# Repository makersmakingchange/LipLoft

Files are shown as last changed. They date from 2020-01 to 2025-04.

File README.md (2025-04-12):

# Liploft

This project was created to enable a person with limited hand function, such as person with quadraplegia, to operate a radio frequency (RF) remote control drone. The project is based on a [LipSync Wireless](https://github.com/makersmakingchange/LipSync-Wireless), an open-source, mouth operated joystick. The user moves the joystick with their lips and mouth and uses sips and puffs of air on the joystick to interact with the drone remote control.

This GitHub repository will serve as a database for all files and documentation associated with the Liploft project. 

This project is a **work in progress**.

## Table of Contents
- [Overview](#overview)
  * [Approach](#approach)
- [Download](#download)
- [Installation and Setup](#installation-and-setup)
  * [LipSync Wireless](#lipsync-wireless)
  * [Liploft Remote Control Interface](#liploft-remote-control-interface)
  * [Software](#software)
- [Operation](#operation)
  * [Pairing](#pairing)
  * [Controlling the Drone with LipSync](#controlling-the-drone-with-lipsync)
- [Contact Us](#contact-us)

<small><i><a href='http://ecotrust-canada.github.io/markdown-toc/'>Table of contents generated with markdown-toc</a></i></small>
  
## Overview
Liploft requires the following components:

1. A drone
2. The drone's remote control, modified to connect with the LipLoft interface.
3. A [Lipsync Wireless](https://github.com/makersmakingchange/LipSync-Wireless) with LipLoft firmware.

### Approach
The Liploft interface is comprised of a microcontroller, a Bluetooth module, and 4 digital potentiometers. The drone's remote controls is modified by removing the two physical joysticks and connecting the digital potetiometers to create virtual, software controllable joysticks. The Liploft acts as a Bluetooth master, connecting to the LipSync Wireless which acts as a Bluetooth slave. Physical movement of and and sips and puffs through the mouthpiece are digitized, transmitted to the Liploft interface and converted into virtual joystick signals.

## Download

 <table style="width:100%">
  <tr>
    <th>Resource</th>
    <th>Version</th>
    <th>Format</th>
    <th>Link</th>
  </tr>
    <tr>
    <td>Liploft All</td>
    <td>Beta 8</td>
    <td>ZIP</td>
    <td><a href="https://github.com/makersmakingchange/LipLoft/archive/master.zip">LipLoft-master.zip</a></td>
  </tr>
  <tr>
    <td>Liploft Manual</td>
    <td>Version 1.0</td>
    <td>PDF</td>
    <td><a href="https://github.com/makersmakingchange/LipLoft/raw/master/LipLoft_User_Manual.pdf">LipLoft_User_Manual.pdf</a></td>
  </tr>
  <tr>
    <td>Liploft BOM (XLSX)</td>
    <td></td>
    <td>XLSX</td>
    <td><a href="https://github.com/makersmakingchange/LipLoft/raw/master/LipLoft_BOM.xlsx">Liploft_BOM.xlsx</a></td>
  </tr>
  <tr>
    <td>Liploft BOM (CSV)</td>
    <td></td>
    <td>CSV</td>
    <td><a href="https://github.com/makersmakingchange/LipLoft/blob/master/LipLoft_BOM.csv" download target="_blank">Liploft_BOM.csv</a></td>
  </tr>
  <tr>
    <td>Lipsync Liploft Firmware</td>
    <td>1.1</td>
    <td>INO</td>
    <td><a href="https://github.com/makersmakingchange/Liploft/raw/master/Software/LipSync_Liploft_Firmware/LipSync_Liploft_Firmware.ino">LipSync_Liploft_Firmware.ino</a></td>
  </tr>
  <tr>
    <td>Liploft Interface Firmware</td>
    <td>1.9</td>
    <td>INO</td>
    <td><a href="https://github.com/makersmakingchange/Liploft/raw/master/Software/Liploft_Interface_Firmware/Liploft_Interface_Firmware.ino">Liploft_Interface_Firmware.ino</a></td>
  </tr>
  <tr>
    <td>Lipsync Manual Bluetooth Config</td>
    <td></td>
    <td>INO</td>
    <td><a href="https://github.com/makersmakingchange/Liploft/raw/master/Software/Liploft_Bluetooth_Config/Lipsync_Bluetooth_Config/Lipsync_Bluetooth_Config.ino">Lipsync_Bluetooth_Config.ino</a></td>
  </tr>
  <tr>
    <td>Interface Manual Bluetooth Config</td>
    <td></td>
    <td>INO</td>
    <td><a href="https://github.com/makersmakingchange/Liploft/raw/master/Software/Liploft_Bluetooth_Config/Interface_Bluetooth_Config/Interface_Bluetooth_Config.ino">Interface_Bluetooth_Config.ino</a></td>
  </tr>
  <tr>
    <td>Liploft Fritzing Board Layout</td>
    <td>Beta 8</td>
    <td>BRD</td>
    <td><a href="https://raw.githubusercontent.com/makersmakingchange/Liploft/master/Hardware/Electronics/Fritzing/Liploft_Breadboard.fzz">Liploft_Breadboard.fzz</a></td>
  </tr>
  <tr>
    <td>Liploft Interface Board Schematic</td>
    <td>Beta 8</td>
    <td>SCH</td>
    <td><a href="https://raw.githubusercontent.com/makersmakingchange/Liploft/master/Hardware/Electronics/Eagle/Liploft_Schematics.sch">Liploft_Schematics.sch</a></td>
  </tr>
  <tr>
    <td rowspan="3">Liploft Housing_design</td>
    <td rowspan="3">V5</td>
    <td rowspan="3">X3G,STL</td>
    <td><a href="https://raw.githubusercontent.com/makersmakingchange/Liploft/master/Hardware/Housing_design/LipSyncDrone/Don_Encl_v5_ABS_L.x3g">Don_Encl_v5_ABS_L.x3g</a></td>
  </tr>
   <tr>
  <td><a href="https://github.com/makersmakingchange/LipLoft/raw/master/Hardware/Housing_design/Liploft_Top.stl">Liploft_Top.STL</a></td>
  </tr>
 <tr>
  <td><a href="https://github.com/makersmakingchange/LipLoft/raw/master/Hardware/Housing_design/Liploft_Bottom.stl">Liploft_Bottom.STL</a></td>
</tr>
 
</tr>
  <tr>
    <td rowspan="8">Lipsync Housing_design</td>
    <td rowspan="8">2.2d</td>
    <td rowspan="8">STL</td>
    <td><a href="https://raw.githubusercontent.com/makersmakingchange/Liploft/master/Hardware/Housing_design/LipSync_Button.STL">LipSync_Button.STL</a></td>
  </tr>
  <tr>
  <td><a href="https://github.com/makersmakingchange/Liploft/raw/master/Hardware/Housing_design/LipSync_Front_Housing.STL">LipSync_Front_Housing.STL</a></td>
  </tr>
  <tr>
  <td><a href="https://github.com/makersmakingchange/Liploft/raw/master/Hardware/Housing_design/LipSync_Joystick_Base.STL">LipSync_Joystick_Base.STL</a></td>
</tr>
<tr>
  <td><a href="https://github.com/makersmakingchange/Liploft/raw/master/Hardware/Housing_design/LipSync_Joystick_Front.STL">LipSync_Joystick_Front.STL</a></td>
</tr>
<tr>
  <td><a href="https://github.com/makersmakingchange/Liploft/raw/master/Hardware/Housing_design/LipSync_Joystick_Rocker.STL">LipSync_Joystick_Rocker.STL</a></td>
</tr>
<tr>
    <td><a href="https://github.com/makersmakingchange/Liploft/raw/master/Hardware/Housing_design/LipSync_Joystick_Stand.STL">LipSync_Joystick_Stand.STL</a></td>
</tr>
 <tr>
  <td><a href="https://github.com/makersmakingchange/LipLoft/raw/master/Hardware/Housing_design/LipSync_Rear_Housing.stl">LipSync_Rear_Housing.STL</a></td>
</tr>
<tr>
  <td><a href="https://raw.githubusercontent.com/makersmakingchange/Liploft/master/Hardware/Housing_design/Print_Settings.txt">Print_Settings.txt</a></td>
</tr>
</table> 

## Installation and Setup

### LipSync Wireless
1. Obtain a [Lipsync Wireless](https://github.com/makersmakingchange/LipSync-Wireless). There are several options for getting a Lipsync Wireless:
 * Build your own. All the necessary files, software, and assembly guides are available in the [Lipsync Wireless GitHub repository](https://github.com/makersmakingchange/LipSync-Wireless). 
 * Submit a build request through the [Makers Making Change website](https://www.makersmakingchange.com/project/lipsyncwireless/). MMC will attempt to pair you with a local volunteer maker to help build and program one. You'll be responsible for covering the cost of materials and shipping. Depending on your location, there may also be pre-built donated units available at little or no cost.
 * [Order a built LipSync](https://www.makersmakingchange.com/order-built-lipsync/) from the Makers Making Change website.
 
 2. It may be helpful to modify the rear housing of the LipSync Wireless so the LED on the Bluetooth module is visible.

### Liploft Remote Control Interface
The remote control interface requires some permanent modifications to the drone's remote control and the addition of several hardware components.

* Setup the circuit in breadboard according to the following diagram:

<p align="center">
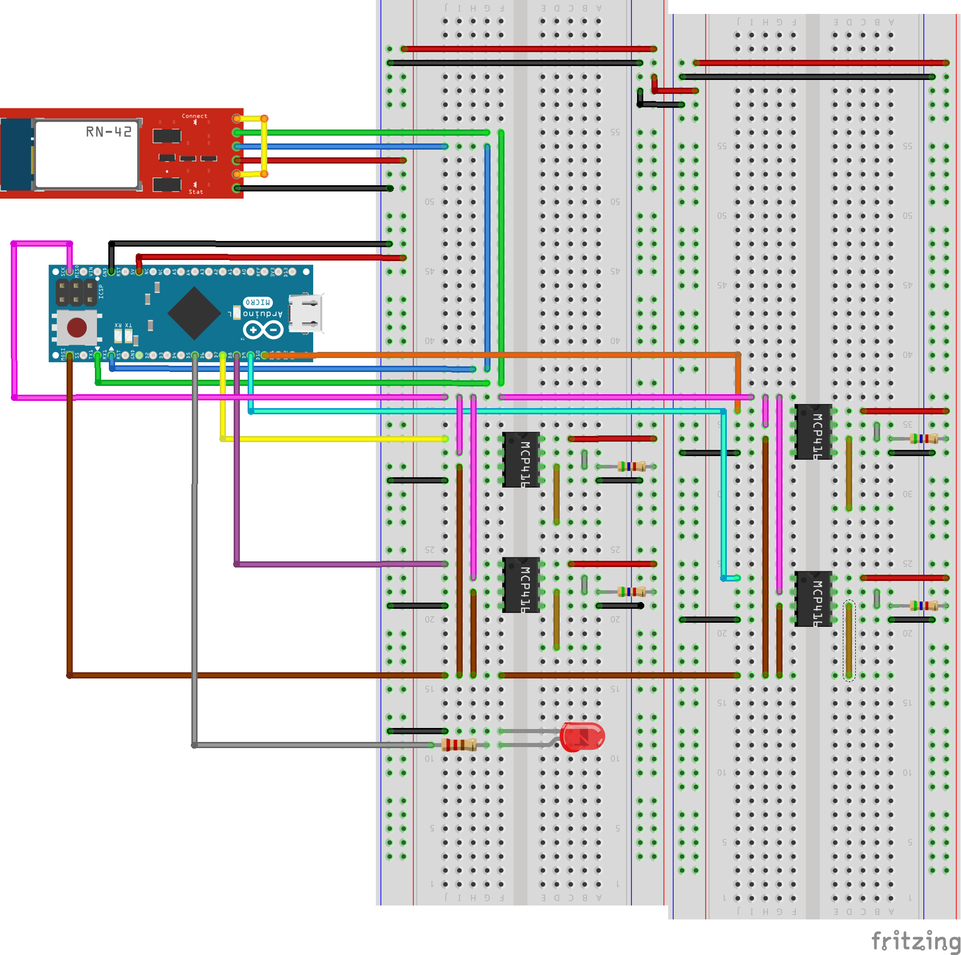
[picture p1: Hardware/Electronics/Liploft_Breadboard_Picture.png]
Liploft Breadboard Picture

</p>

* Setup the Bluetooth circuit in breadboard according to the following diagram:
  * Bluetooth module RTS pin to Bluetooth module CTS
  * Bluetooth module RX pin to Arduino TX pin 
  * Bluetooth module TX pin to Arduino RX pin 
  * Bluetooth module VCC pin to Arduino 5V pin 
  * Bluetooth module GND pin to Arduino GND pin 
  
  <p align="center">
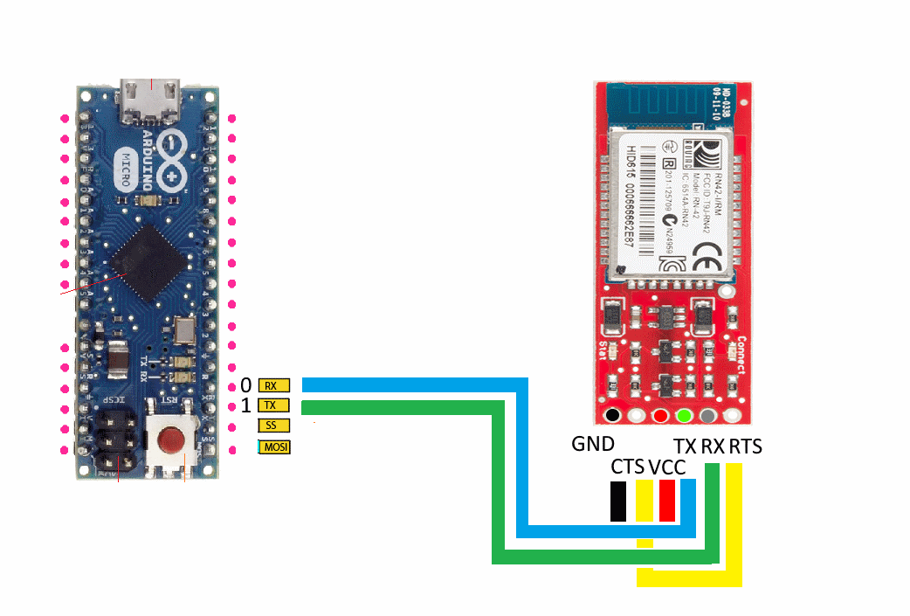
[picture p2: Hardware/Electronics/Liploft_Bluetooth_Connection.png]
Liploft Bluetooth Connection

</p>

* Setup the rest of circuit in breadboard according to the following diagram:
  * MCP4261 IC1 pin 1 to Arduino pin 10
  * MCP4261 IC2 pin 1 to Arduino pin 9
  * MCP4261 IC3 pin 1 to Arduino pin 8
  * MCP4261 IC4 pin 1 to Arduino pin 7
  * Led pin to Arduino pin 5
  * MCP4261 IC1,IC2,IC3,IC4 pin 2 to Arduino pin SCK
  * MCP4261 IC1,IC2,IC3,IC4 pin 3 to Arduino pin MOSI
  * MCP4261 IC1,IC2,IC3,IC4 pin 4 to Arduino pin GND
  * MCP4261 IC1,IC2,IC3,IC4 pin 5 to Arduino pin GND
  * MCP4261 IC1,IC2,IC3,IC4 pin 6 to channels of transmiter (potemtiometer) and same MCP4261 pin 7
  * MCP4261 IC1,IC2,IC3,IC4 pin 7 to 5.6K resistor and Arduino pin 5V in pullup configuration 
  * MCP4261 IC1,IC2,IC3,IC4 pin 8 to Arduino pin 5V
  
   <p align="center">
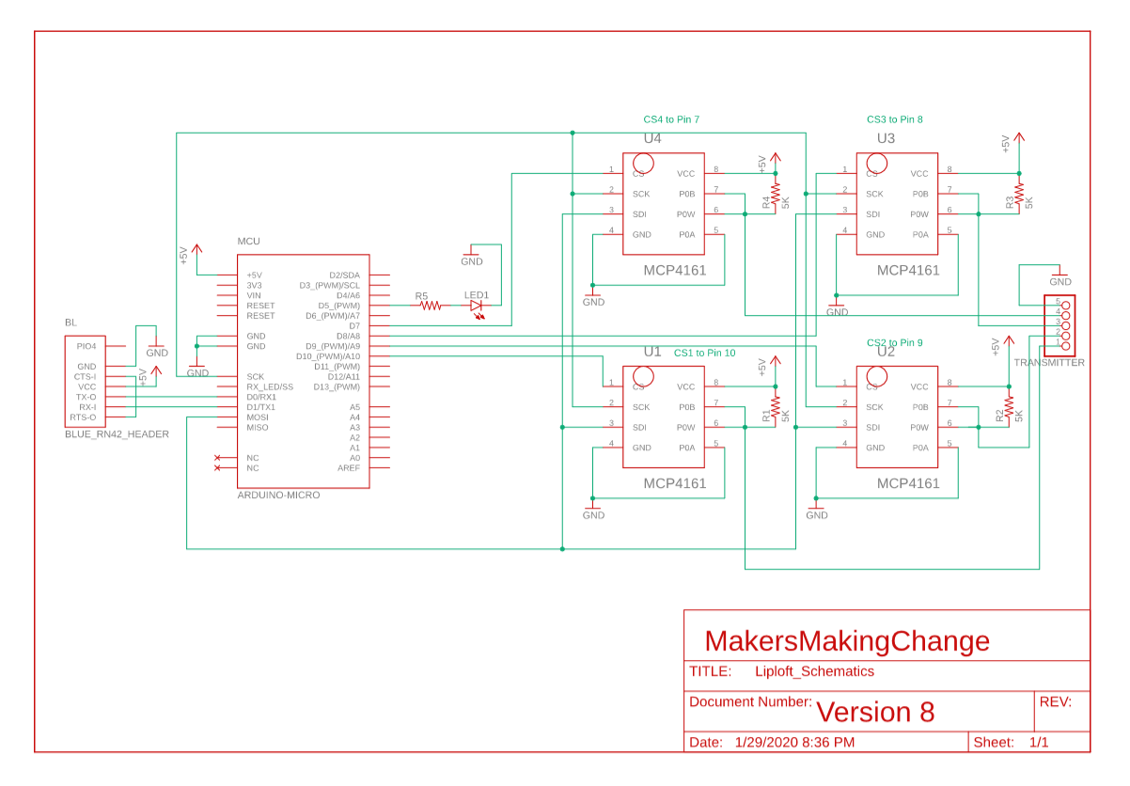
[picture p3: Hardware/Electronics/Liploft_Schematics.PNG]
Liploft Schematics

</p>

* Setup the circuit for controller connection according to the following example:

<p align="center">
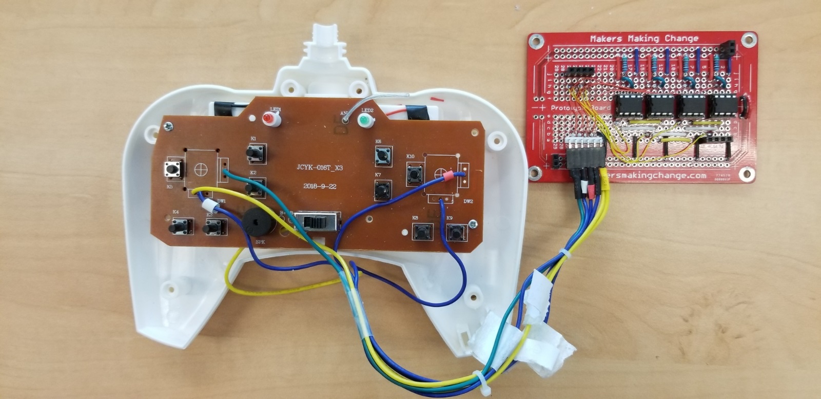
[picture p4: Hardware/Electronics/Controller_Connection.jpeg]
Liploft Controller Connection Picture

</p>

### Software
The Lipsync Wireless and Liploft interface require firmware.

*	Download the necessary files from the LipLoft GitHub repository.
  1. Visit LipLoft GitHub repository at https://github.com/makersmakingchange/LipLoft
  2. Click on “Clone or download” button” in green.
  3. Click on “Download Zip” to download the necessary file.
  4. Extract “LipLoft-master.zip” to the directory of your choice.
*	Download and install MCP4261 Arduino library 
  1. Visit MCP4261 library GitHub repository at https://github.com/dreamcat4/Mcp4261
  2. Click on “Clone or download” button” in green.
  3. Click on “Download Zip” to download the necessary file.
  4. Extract “Mcp4261-master.zip” to the directory of your choice.
  5. Rename “Mcp4261-master.zip” to “Mcp4261.zip”
  6. Open Arduino IDE
  7. Click on Sketch > Include Library > Add .zip Library
  8. Select “Mcp4261.zip”
 *	Upload Lipsync firmware 
  1. Connect the Lipsync Wireless to the computer using the USB cable.
  2. Verify and upload "LipSync_Liploft_Firmware.ino" to the Lipsync Wireless unit using Arduino IDE
  * Upload Liploft firmware
  1. Connect the Liploft interface to the computer using a USB cable.
  2. Verify and upload "Liploft_Interface_Firmware.ino" to the Liploft interface unit using Arduino IDE

## Operation

### Pairing
  1. Connect power to the LipSync Wireless by plugging in the USB cable to a power pack or other power source.
  2. Wait for 5 seconds. (You need to power the LipSync (Slave Bluetooth module) 5 seconds before the LipLoft unit (Master Bluetooth module) if you are connecting the LipSync to LipLoft for the first time.)
  3. Connect power to the LipLoft unit. The red LED on Bluetooth modules should start blinking faster and the green led on both Bluetooth modules should stay on to indicate connection is established between Lipsync and Liploft.
  
If the connection is not established, you can use code to manually configure the Bluetooth modules. The Bluetooth module in the Lipsync Wirelss can be reconfigured using "Lipsync_Bluetooth_Config.ino" code and the Bluetooth module in the Liploft interface unit can be reconfigured using "Interface_Bluetooth_Config.ino" code. You will need to upload both codes at the same time. The green led on both Bluetooth modules will stay on once the connection is established.

### Controlling the Drone with LipSync
* Arm the drone by puffing and sipping once (the LED on the Liploft Interface will turn on to indicate it is armed.)
* sip/puff controls the throttle
* LipSync joystick controls pitch and roll
* Gyro calibration is automated

<!-- ABOUT MMC START -->
## About Makers Making Change
[Makers Making Change Logo](https://www.makersmakingchange.com/)

Makers Making Change is a program of [Neil Squire](https://www.neilsquire.ca/), a Canadian non-profit that uses technology, knowledge, and passion to empower people with disabilities.

Makers Making Change leverages the capacity of community based Makers, Disability Professionals and Volunteers to develop and deliver affordable Open Source Assistive Technologies.

 - Website: [www.MakersMakingChange.com](https://www.makersmakingchange.com/)
 - GitHub: [makersmakingchange](https://github.com/makersmakingchange)
 - Bluesky: [@makersmakingchange.bsky.social](https://bsky.app/profile/makersmakingchange.bsky.social)
 - Instagram: [@makersmakingchange](https://www.instagram.com/makersmakingchange)
 - Facebook: [makersmakechange](https://www.facebook.com/makersmakechange)
 - LinkedIn: [Neil Squire Society](https://www.linkedin.com/company/neil-squire-society/)
 - Thingiverse: [makersmakingchange](https://www.thingiverse.com/makersmakingchange/about)
 - Printables: [MakersMakingChange](https://www.printables.com/@MakersMakingChange)

### Contact Us
For technical questions, to get involved, or to share your experience we encourage you to [visit our website](https://www.makersmakingchange.com/) or [contact us](https://www.makersmakingchange.com/s/contact).
<!-- ABOUT MMC END -->

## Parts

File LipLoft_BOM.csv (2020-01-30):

Qty | Component | Component name (August 12, 2019) | Line Item | Manufacturer | COO | MPN | SKU | SKU | SKU | SKU | SKU | SKU | SKU | SKU | URL ( Canada ) | URL ( United States )
 |  |  |  |  |  |  | Digi-Key | Mouser | Qosina | Cole-Parmer | Lee Spring | U.S. Plastic Corp. | B&H Photo | Amazon
1 | Required | Arduino Micro | A000053 | Arduino | Italy | A000053 | 1050-1066-ND | 782-A000053 |  |  |  |  |  |  | https://www.digikey.ca/product-detail/en/arduino/A000053/1050-1066-ND | https://www.digikey.com/product-detail/en/arduino/A000053/1050-1066-ND
1 | Required | SparkFun Bluetooth Mate Silver | WRL-12576 | SparkFun Electronics | Italy | WRL-12576 | 1568-1265-ND |  |  |  |  |  |  |  | https://www.digikey.ca/product-detail/en/sparkfun-electronics/WRL-12576/1568-1265-ND/5762415 | https://www.digikey.com/product-detail/en/sparkfun-electronics/WRL-12576/1568-1265-ND/5762415
4 | Required | MCP4261 Digital potemtiometer |  | Microchip |  | MCP4261
4 | Required | RES 5.6K OHM 1/4W 5% AXIAL |  | Yageo |  | CFR-25JB-52-5K6 | 5.6KQBK-ND |  |  |  |  |  |  |  | https://www.digikey.ca/product-detail/en/yageo/CFR-25JB-52-5K6/5.6KQBK-ND/2243
1 | Required | LED GREEN CLEAR 5MM ROUND |  | Cree |  | C566C-GFF-CX0Y0892 | C566C-GFF-CX0Y0892CT-ND |  |  |  |  |  |  |  | https://www.digikey.ca/product-detail/en/cree-inc/C566C-GFF-CX0Y0892/C566C-GFF-CX0Y0892CT-ND/6138564
1 | Required | 300 Ohm 1/4W Axial Through-Hole Resistor | CF14JT300R | Stackpole Electronics | China | CF14JT300R | CF14JT300RCT-ND |  |  |  |  |  |  |  | https://www.digikey.ca/product-detail/en/stackpole-electronics-inc/CF14JT300R/CF14JT300RCT-ND | https://www.digikey.com/product-detail/en/stackpole-electronics-inc/CF14JT300R/CF14JT300RCT-ND

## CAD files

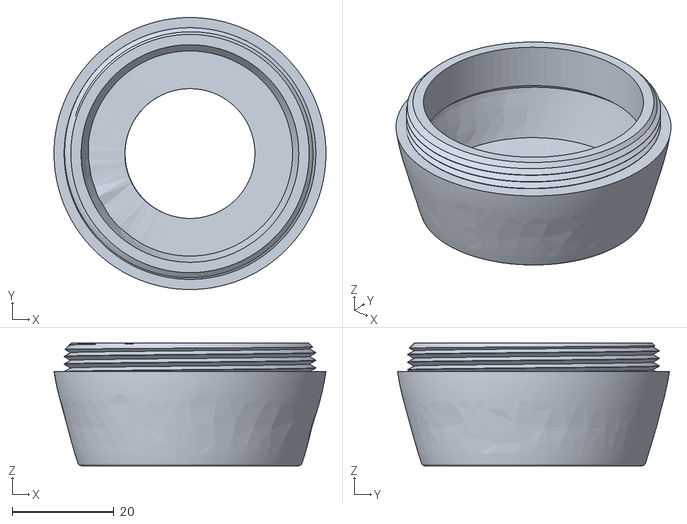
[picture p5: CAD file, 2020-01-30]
Hardware/Housing_design/LipSync_Front_Housing.STL
53.4 x 53.4 x 24.1

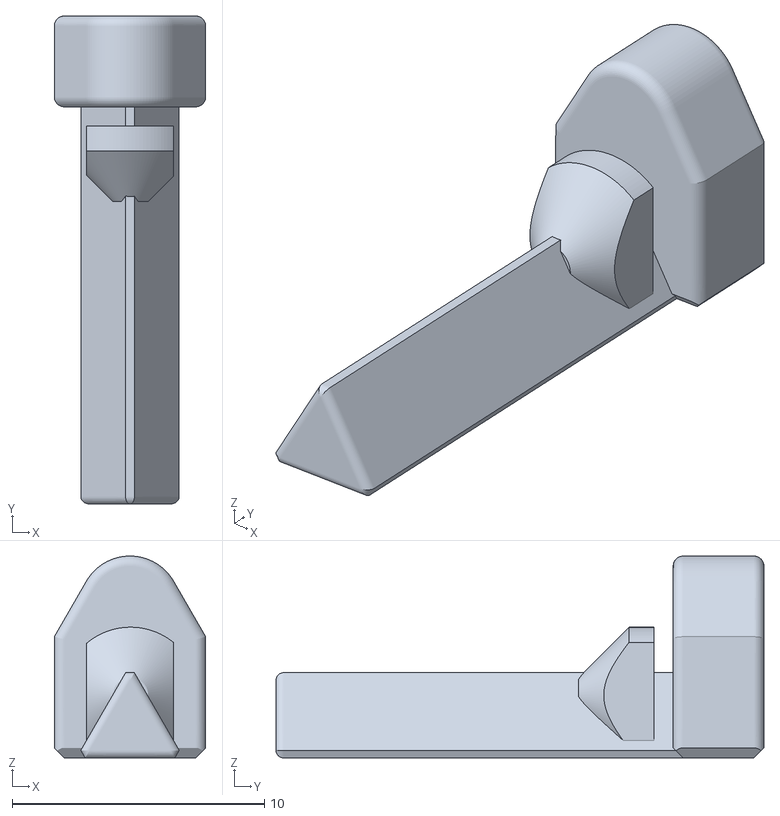
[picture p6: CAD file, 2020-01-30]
Hardware/Housing_design/LipSync_Button.stl
6.00 x 19.3 x 8.00

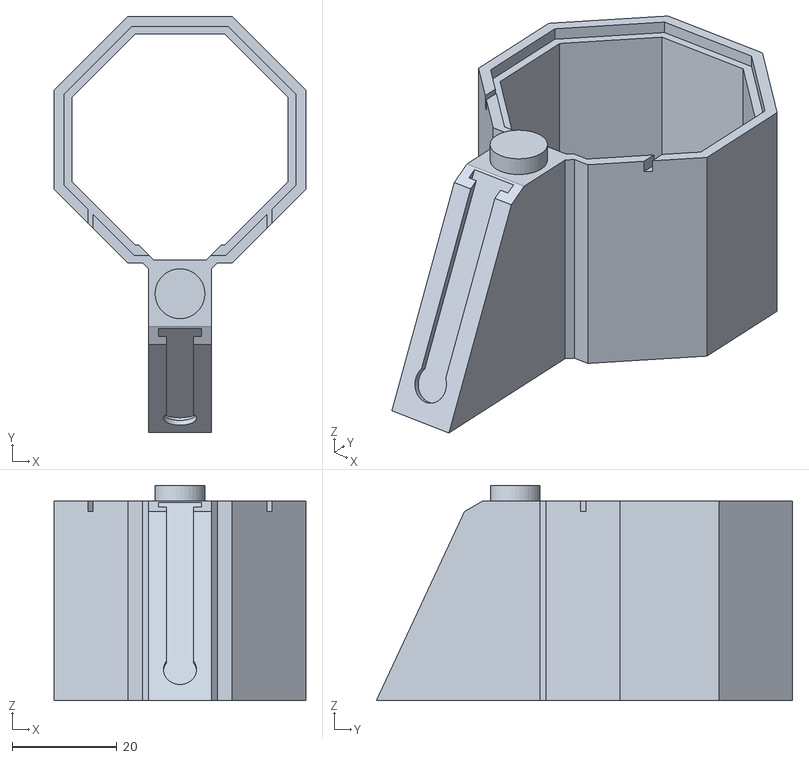
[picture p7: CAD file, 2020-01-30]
Hardware/Housing_design/LipSync_Joystick_Stand.STL
48.0 x 79.3 x 41.0

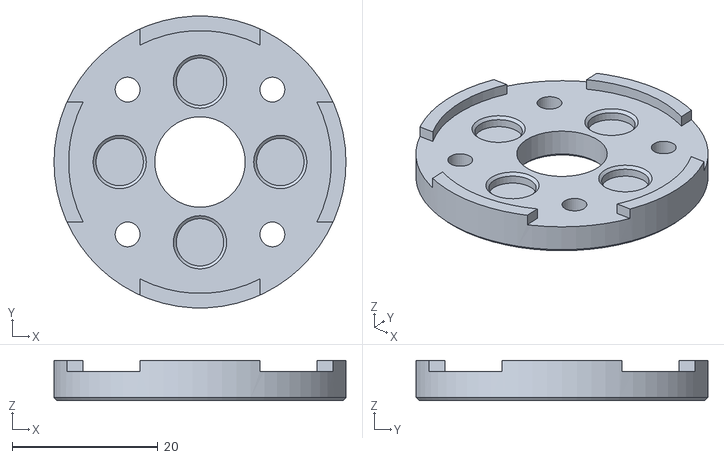
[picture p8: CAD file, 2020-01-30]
Hardware/Housing_design/LipSync_Joystick_Front.STL
40.0 x 39.9 x 5.50

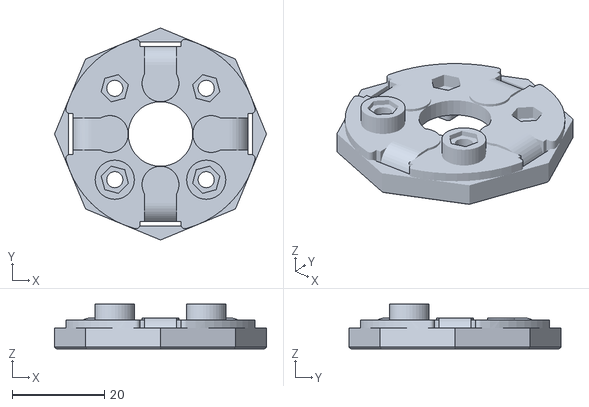
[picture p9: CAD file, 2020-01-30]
Hardware/Housing_design/LipSync_Joystick_Base.STL
46.0 x 46.0 x 9.75

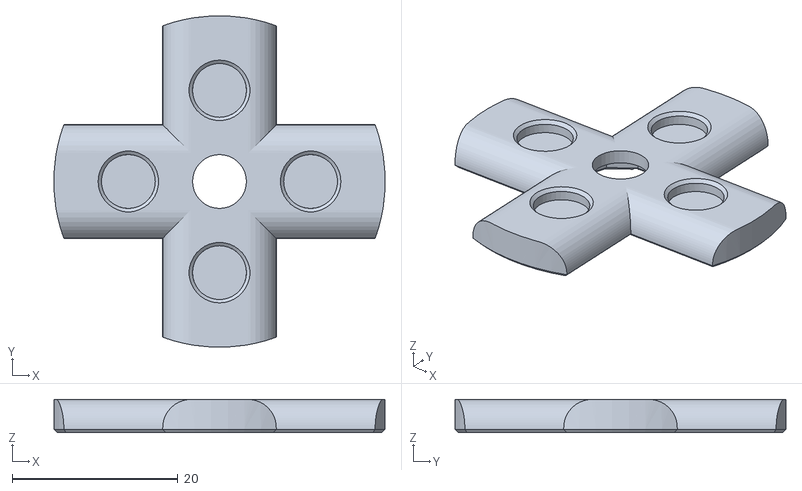
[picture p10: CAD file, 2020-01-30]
Hardware/Housing_design/LipSync_Joystick_Rocker.STL
40.0 x 40.0 x 4.00

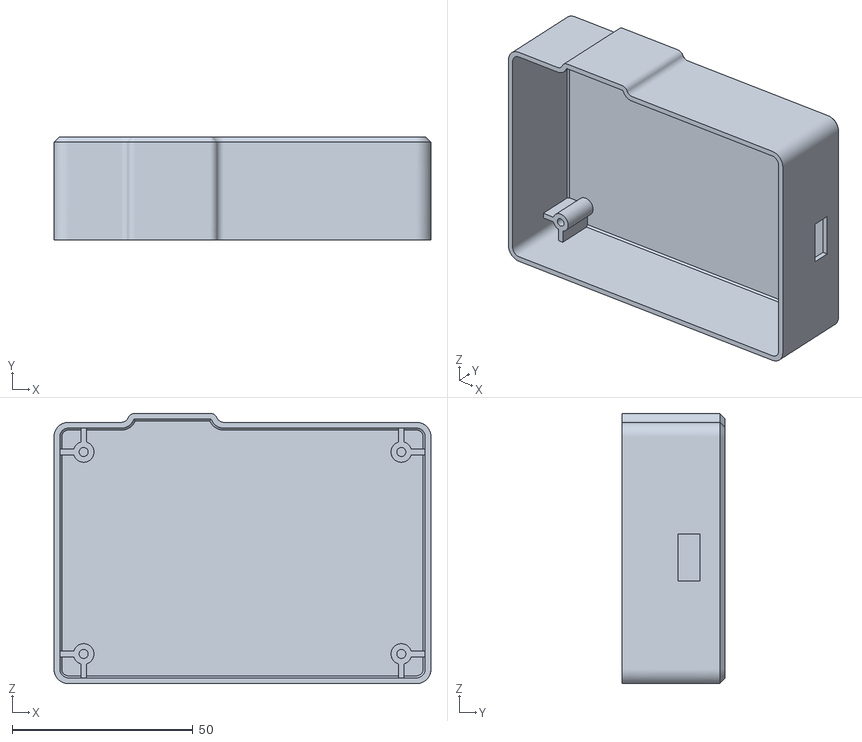
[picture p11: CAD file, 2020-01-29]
Hardware/Housing_design/Liploft_Bottom.stl
104.3 x 28.6 x 74.8

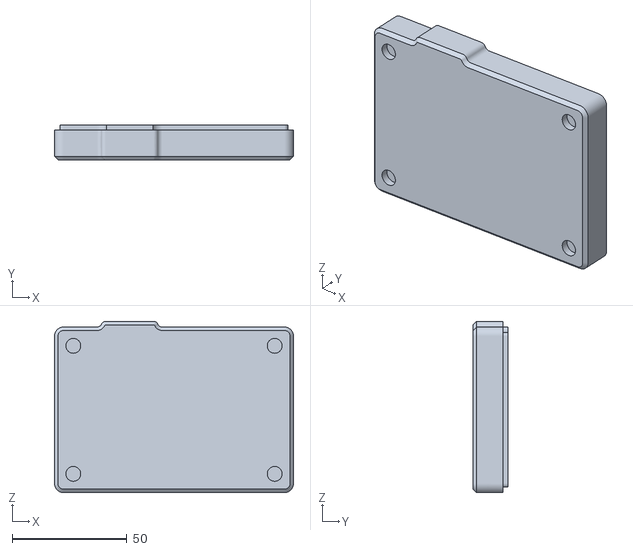
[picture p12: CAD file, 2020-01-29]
Hardware/Housing_design/Liploft_Top.stl
104.3 x 15.1 x 74.8

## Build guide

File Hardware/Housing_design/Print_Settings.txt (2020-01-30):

Print all components in orientation of STL file.

----------------------------
First print:
LipSync_Front_Housing
LipSync_Rear_Housing
LipSync_Button (2 are needed)
LipSync_Joystick_Stand

Infill: 20%
Layer Height: 0.2mm
Support Material: No
Raft: No
----------------------------

----------------------------
Second print:
LipSync_Joystick_Front_Plate
LipSync_Joystick_Rocker
LipSync_Joystick_Base

Infill: 50%
Layer Height: 0.2mm
Support Material: Yes
Raft: No
----------------------------

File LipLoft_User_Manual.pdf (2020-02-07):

## LipLoft User Manual Version 1.0

- Power the LipSync (Slave module)
- Power the LipLoft interface unit (Master module)

Note: Power the LipSync (Slave module) 5 seconds before the LipLoft interface unit (Master module) if you are connecting the LipSync to LipLoft for the first time.

- The green led on bluetooth module of the LipLoft interface indicates if the connection between LipSync and LipLoft interface unit is established.
- The green led on bluetooth module of the LipLoft interface should stay ON. You can disconnect the power source from LipLoft interface and power again LipLoft interface if the led is OFF. This should help to establish bluetooth connection.

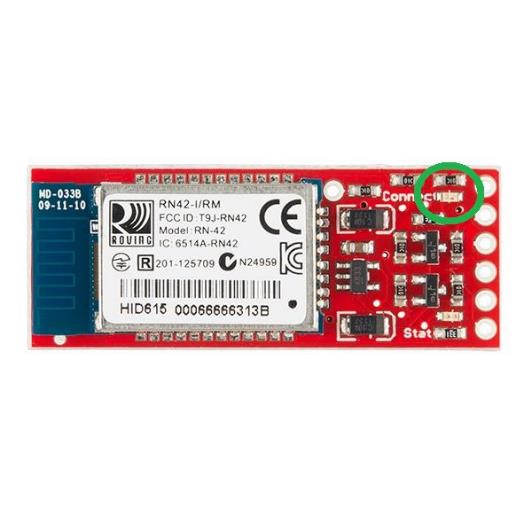
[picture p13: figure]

- Next you need to Arm the drone. Arming allows the motors to start spinning. Make sure all objects, people and any body parts are out of the way before Arming the drone.
- Arm the drone by puffing and sipping once. The main external green led will turn on and stay on to indicate the drone is Armed.
- Sip and puff control the throttle

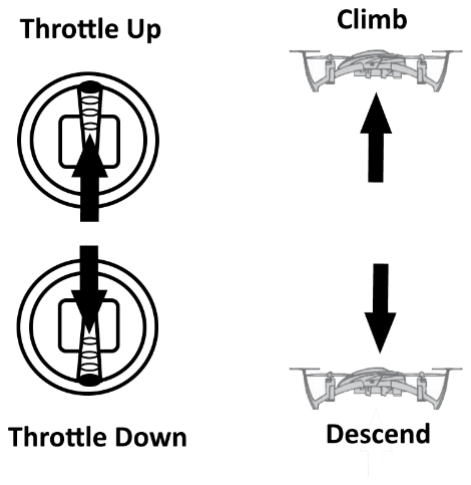
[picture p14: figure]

Action | Result
Puff | Throttle up ( Increases throttle value )
Sip | Throttle down ( Decreases throttle value )

Note: You can sip to float the drone for 1 second and continue sipping to land the drone.

- LipSync joystick controls pitch and roll

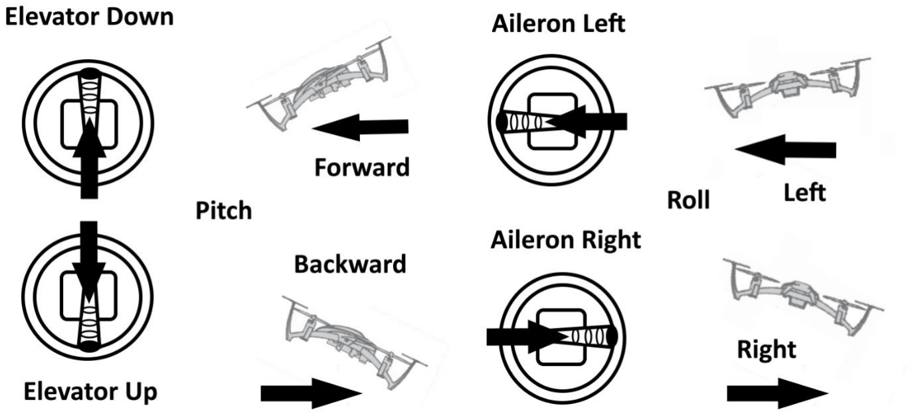
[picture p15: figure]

Lipsync Action | Visual Action | Drone Action
Mouthpiece Right | | Roll Right
Mouthpiece Left | | Roll Left
Mouthpiece Up | | Move Forward
Mouthpiece Down | | Move Backward
- Gryo calibration is automated when the drone is Armed.
- Land the drone and power Off the LipLoft interface unit for ending the usage.
- Disconnect the power in the drone and finally disconnect Lipsync power connection.

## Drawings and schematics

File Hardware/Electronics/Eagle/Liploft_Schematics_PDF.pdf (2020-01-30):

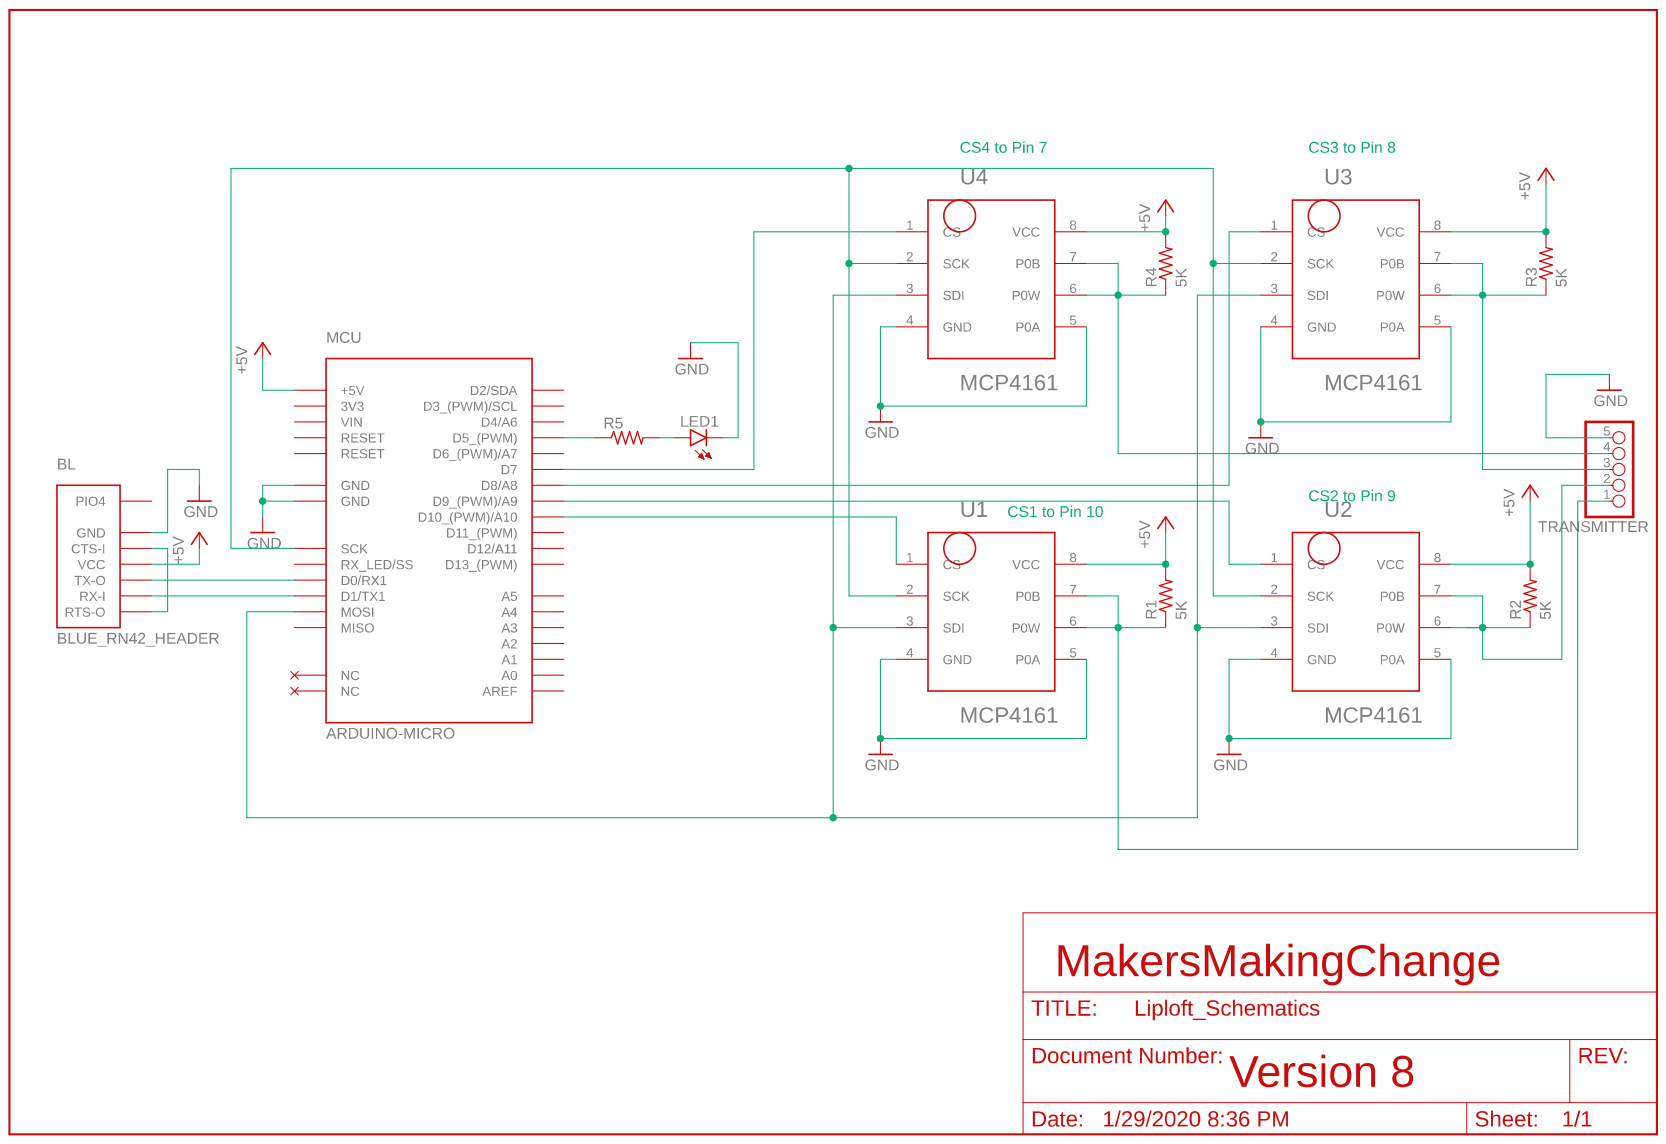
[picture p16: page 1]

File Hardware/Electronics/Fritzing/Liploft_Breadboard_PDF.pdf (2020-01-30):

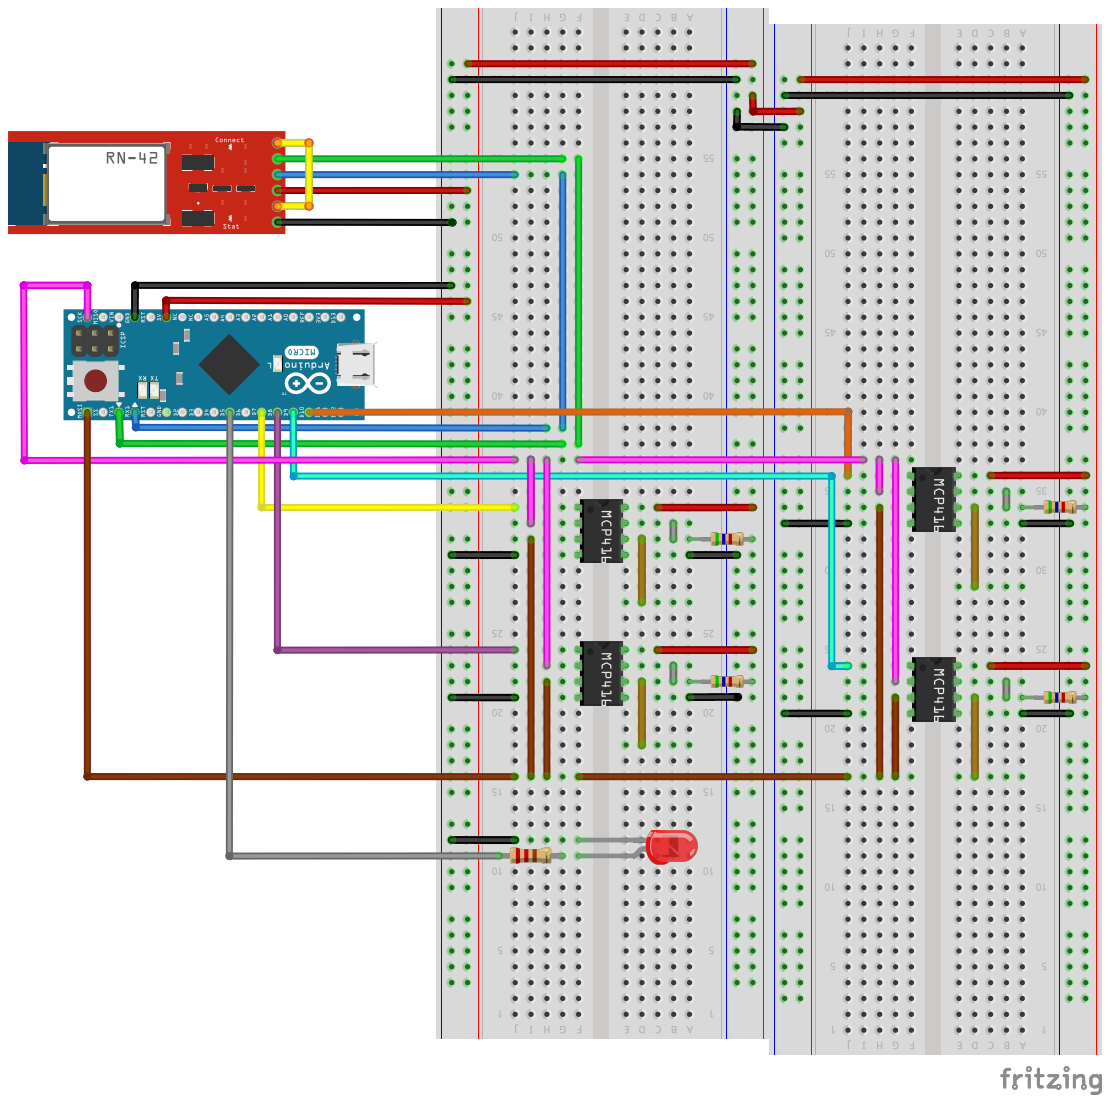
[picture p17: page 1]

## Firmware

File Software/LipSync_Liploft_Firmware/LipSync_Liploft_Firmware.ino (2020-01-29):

/*
//                                                                                                  
//  +++         .+++:    /++++++++/:.     .:/+++++/: .+++/`     .+++/  ++++.      ++++.     `-/++++++/:
//  oooo         .ooo:    +ooo:--:+ooo/   :ooo/:::/+/  -ooo+`   .ooo+`  ooooo:     .o-o`   `/ooo+//://+:
//  oooo         .ooo:    +ooo`    :ooo-  oooo`     `   .ooo+` .ooo+`   oooooo/`   .o-o`  .oooo-`       
//  oooo         .ooo:    +ooo`    -ooo-  -ooo+:.`       .ooo+.ooo/`    ooo:/oo+.  .o-o`  +ooo.         
//  oooo         .ooo:    +ooo.`..:ooo+`   `:+oooo+:`     `+ooooo/      ooo: :ooo- .o-o`  oooo          
//  oooo         .ooo:    +ooooooooo+:`       `-:oooo-     `+ooo/       ooo/  .+oo/.o-o`  +ooo.         
//  oooo         .ooo:    +ooo-...``             `oooo      /ooo.       ooo/   `/oo-o-o`  .oooo-        
//  oooo::::::.  .ooo:    +ooo`           :o//:::+ooo:      /ooo.       ooo/     .o-o-o`   ./oooo/:::/+/
//  +ooooooooo:  .ooo:    /ooo`           -/++ooo+/:.       :ooo.       ooo:      `.o.+      `-/+oooo+/-
//
//An assistive technology device which is developed to allow quadriplegics to operate drones by manipulation of a mouth-operated joystick with integrated sip and puff controls.
*/

//Developed by : MakersMakingChange + UBC hackathon team
//Firmware : LipSync_LipLoft_Firmware
//VERSION: 1.1 (23 Jan 2020) 


#include <EEPROM.h>
#include <math.h>


#define DEBUG_MODE true                           //Debug mode ( Enabled = true and Disabled = false )

//***PIN ASSIGNMENTS***//
#define MODE_SELECT_PIN 12                        // LipSync Mode Select
#define BUTTON_UP_PIN 8                           // Control Button 1: UP - digital input pin 8 (internally pulled-up)
#define BUTTON_DOWN_PIN 7                         // Control Button 2: DOWN - digital input pin 7 (internally pulled-up)
#define LED_1_PIN 4                               // LipSync LED Color1 : GREEN - digital output pin 5
#define LED_2_PIN 5                               // LipSync LED Color2 : RED - digital outputpin 4

#define TRANS_CONTROL_PIN A3                      // Bluetooth Transistor Control Pin - digital output pin A3
#define PIO4_PIN A4                               // Bluetooth PIO4_PIN Command Pin - digital output pin A4

#define PRESSURE_PIN A5                           // Sip & Puff Pressure Transducer Pin - analog input pin A5
#define X_DIR_HIGH_PIN A0                         // X Direction High (Cartesian positive x : right) - analog input pin A0
#define X_DIR_LOW_PIN A1                          // X Direction Low (Cartesian negative x : left) - digital output pin A1
#define Y_DIR_HIGH_PIN A2                         // Y Direction High (Cartesian positive y : up) - analog input pin A2
#define Y_DIR_LOW_PIN A10                         // Y Direction Low (Cartesian negative y : down) - analog input pin A10

//***CUSTOMIZE VALUES***//

#define RAW_PRESSURE_THRESHOLD 100                 //Sip/Puff threashold for raw bt mode

#define BT_CONFIG_FLAG false                      //Configure bluetooth ( Configure = true and Not Configure = false ). This is used to reset bluetooth module
#define JOYSTICK_DEFAULT_SPEED 30                 //Maximum default speed  (Not used)   
#define JOYSTICK_DELTA_SPEED 5                    //Delta value that is used to calculate speed levels (Not used)  
#define JOYSTICK_RADIUS 30.0                      //Constant joystick radius


//***VARIABLE DECLARATION***//

int joystickSpeedCounter = 5;                       //Cursor speed counter which is set to 4 by default (Not used)  


int xHigh, yHigh, xLow, yLow;                       
int xRight, xLeft, yUp, yDown;

int spNeutral;                                    //Individual neutral starting positions for each FSR

int xHighMax, xLowMax, yHighMax, yLowMax;         //Max FSR values which are set to the values from EEPROM


float xHighYHighRadius, xHighYLowRadius, xLowYLowRadius, xLowYHighRadius;
float xHighYHigh, xHighYLow, xLowYLow, xLowYHigh;


int commMode = 0;                                 
int bluetoothConfigDone;                          // Binary check of completed Bluetooth configuration (Not Used)
unsigned int puffCount, sipCount;                 //The puff and long sip incremental counter variables
int pollCounter = 0;                              //poll counter


float yHighDebug, yLowDebug, xHighDebug, xLowDebug;

//Pressure sensor variables
float sipThreshold, puffThreshold;

//Drone Speed Level structure 
typedef struct {
  int _delay;
  float _factor;
  int _maxSpeed;
} _joystick;

//Define characteristics of each speed level ( Example: 5,-1.0,10,2 ) (Not used)
_joystick setting1 = {5, -1.1, JOYSTICK_DEFAULT_SPEED - (5 * JOYSTICK_DELTA_SPEED)};
_joystick setting2 = {5, -1.1, JOYSTICK_DEFAULT_SPEED - (4 * JOYSTICK_DELTA_SPEED)};
_joystick setting3 = {5, -1.1, JOYSTICK_DEFAULT_SPEED - (3 * JOYSTICK_DELTA_SPEED)};
_joystick setting4 = {5, -1.1, JOYSTICK_DEFAULT_SPEED - (2 * JOYSTICK_DELTA_SPEED)};
_joystick setting5 = {5, -1.1, JOYSTICK_DEFAULT_SPEED - (JOYSTICK_DELTA_SPEED)};
_joystick setting6 = {5, -1.1, JOYSTICK_DEFAULT_SPEED};
_joystick setting7 = {5, -1.1, JOYSTICK_DEFAULT_SPEED + (JOYSTICK_DELTA_SPEED)};
_joystick setting8 = {5, -1.1, JOYSTICK_DEFAULT_SPEED + (2 * JOYSTICK_DELTA_SPEED)};
_joystick setting9 = {5, -1.1, JOYSTICK_DEFAULT_SPEED + (3 * JOYSTICK_DELTA_SPEED)};
_joystick setting10 = {5, -1.1, JOYSTICK_DEFAULT_SPEED + (4 * JOYSTICK_DELTA_SPEED)};
_joystick setting11 = {5, -1.1, JOYSTICK_DEFAULT_SPEED + (5 * JOYSTICK_DELTA_SPEED)};

_joystick joystickParams[11] = {setting1, setting2, setting3, setting4, setting5, setting6, setting7, setting8, setting9, setting10, setting11};

int single = 0;
int puff1, puff2;

bool settingsEnabled = false; 

//-----------------------------------------------------------------------------------//

//***MICROCONTROLLER AND PERIPHERAL MODULES CONFIGURATION***//

void setup() {
  
  Serial.begin(115200);                           //Setting baud rate for serial communication which is used for diagnostic data returned from Bluetooth and microcontroller
  Serial1.begin(115200);                          //Setting baud rate for Bluetooth AT command 

  pinMode(LED_1_PIN, OUTPUT);                     //Set the LED pin 1 as output(GREEN LED)
  pinMode(LED_2_PIN, OUTPUT);                     //Set the LED pin 2 as output(RED LED)
  pinMode(TRANS_CONTROL_PIN, OUTPUT);             //Set the transistor pin as output
  pinMode(PIO4_PIN, OUTPUT);                      //Set the bluetooth command mode pin as output

  pinMode(PRESSURE_PIN, INPUT);                   //Set the pressure sensor pin input
  pinMode(X_DIR_HIGH_PIN, INPUT);                 //Define Force sensor pinsas input ( Right FSR )
  pinMode(X_DIR_LOW_PIN, INPUT);                  //Define Force sensor pinsas input ( Left FSR )
  pinMode(Y_DIR_HIGH_PIN, INPUT);                 //Define Force sensor pinsas input ( Up FSR )
  pinMode(Y_DIR_LOW_PIN, INPUT);                  //Define Force sensor pinsas input ( Down FSR )

  pinMode(MODE_SELECT_PIN, INPUT_PULLUP);     
  pinMode(BUTTON_UP_PIN, INPUT_PULLUP); 
  pinMode(BUTTON_DOWN_PIN, INPUT_PULLUP);

  pinMode(2, INPUT_PULLUP);                       //Set unused pins as inputs with pullups
  pinMode(3, INPUT_PULLUP);
  pinMode(9, INPUT_PULLUP);
  pinMode(11, INPUT_PULLUP);
  pinMode(13, INPUT_PULLUP);

  if(DEBUG_MODE==true) {
    Serial.println("Beginning initialization...");
  }


  joystickInitialization();                       //Set the Home joystick and generate movement threshold boundaries
  delay(10);
  pressureSensorInitialization();                 //Set the pressure sensor threshold boundaries
  delay(10);
  setDefault();                                   //Set the default values that are stored in EEPROM
  delay(10);
  bluetoothConfigure();                           //Conditionally configure the Bluetooth module
  delay(10);
  if(DEBUG_MODE==true) {Serial.println("Initialization complete.");}
  
  ledBlink(4, 250, 3);                            //End initialization visual feedback

  displayVersion();                               //Display firmware version number

  //Functions below are for diagnostic feedback only
  if(DEBUG_MODE==true) {
      Serial.println((String)"bluetoothConfigDone: "+EEPROM.get(0, puff1));
      delay(5);
      Serial.println((String)"yHighComp: "+EEPROM.get(6, yHighDebug));
      delay(5);
      Serial.println((String)"yLowComp: "+EEPROM.get(10, yLowDebug));
      delay(5);
      Serial.println((String)"xHighComp: "+EEPROM.get(14, xHighDebug));
      delay(5);
      Serial.println((String)"xLowComp: "+EEPROM.get(18, xLowDebug));
      delay(5);
  }

}

//-----------------------------------------------------------------------------------//

//***START OF MAIN LOOP***//

void loop() {

  settingsEnabled=serialSettings(settingsEnabled);       //Check to see if setting option is enabled in Lipsync

  xHigh = (float)analogRead(X_DIR_HIGH_PIN);             //Read analog values of FSR's : A0
  xLow = (float)analogRead(X_DIR_LOW_PIN);               //Read analog values of FSR's : A1
  yHigh = (float)analogRead(Y_DIR_HIGH_PIN);             //Read analog values of FSR's : A0
  yLow = (float)analogRead(Y_DIR_LOW_PIN);               //Read analog values of FSR's : A10
  
  xHighYHigh = sqrt(sq(((xHigh - xRight) > 0) ? (float)(xHigh - xRight) : 0.0) + sq(((yHigh - yUp) > 0) ? (float)(yHigh - yUp) : 0.0));     //The sq() function raises thr input to power of 2 and is returning the same data type int->int
  xHighYLow = sqrt(sq(((xHigh - xRight) > 0) ? (float)(xHigh - xRight) : 0.0) + sq(((yLow - yDown) > 0) ? (float)(yLow - yDown) : 0.0));    //The sqrt() function raises input to power 1/2, returning a float type
  xLowYHigh = sqrt(sq(((xLow - xLeft) > 0) ? (float)(xLow - xLeft) : 0.0) + sq(((yHigh - yUp) > 0) ? (float)(yHigh - yUp) : 0.0));          //These are the vector magnitudes of each quadrant 1-4. Since the FSRs all register
  xLowYLow = sqrt(sq(((xLow - xLeft) > 0) ? (float)(xLow - xLeft) : 0.0) + sq(((yLow - yDown) > 0) ? (float)(yLow - yDown) : 0.0));         //a larger digital value with a positive application force, a large negative difference

  //Check to see if the joystick has moved
  if ((xHighYHigh > xHighYHighRadius) || (xHighYLow > xHighYLowRadius) || (xLowYLow > xLowYLowRadius) || (xLowYHigh > xLowYHighRadius)) {
    //Add to the poll counter
    pollCounter++;
    delay(20); 
    if (pollCounter >= 3) {
       sendRawBTPacket(0, (int)xHigh, (int)xLow, (int)yHigh, (int)yLow);
    }
  }
  //Perform buttons functions
  processButtonInput();

  //Perform pressure sensor sip and puff functions
  processRawPressureInput();
}

//***END OF Main LOOP***//

//-----------------------------------------------------------------------------------//

//***BUTTON INPUT PROCESSING***//

void processButtonInput()
{
    if (digitalRead(BUTTON_UP_PIN) == LOW) {
    delay(200);
    ledClear();
    delay(50);
    if (digitalRead(BUTTON_DOWN_PIN) == LOW) {
      joystickManualCalibration();                      //Call joystick calibration if both push button up and down are pressed 
    } 
  }

  if (digitalRead(BUTTON_DOWN_PIN) == LOW) {
    delay(200);
    ledClear();
    delay(50);
    if (digitalRead(BUTTON_UP_PIN) == LOW) {
      joystickManualCalibration();                      //Call joystick calibration if both push button up and down are pressed 
    } 
  }
}

//***PRESSURE INPUT PROCESSING***//

void processRawPressureInput()
{
  int value = analogRead(PRESSURE_PIN);
  if (value > spNeutral - RAW_PRESSURE_THRESHOLD && value < spNeutral + RAW_PRESSURE_THRESHOLD)
  {
    return;
  }
  sendRawBTPacket(2, value);
}
//***END OF INPUT PROCESSING***//

//-----------------------------------------------------------------------------------//
//***SERIAL SETTINGS FUNCTION TO CHANGE SPEED AND COMMUNICATION MODE USING SOFTWARE***//
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

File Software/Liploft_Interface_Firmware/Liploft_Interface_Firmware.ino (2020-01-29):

//Developed by : MakersMakingChange + UBC hackathon team
//Firmware : Liploft_Interface_Firmware
//VERSION: 1.9 (23 Jan 2020) 

//HOW TO CONTROL THE DRONE: 

//Arm the drone by puffing and sipping once
//sip/puff controls the throttle
//LipSync joystick controls pitch and roll (working well)
//gryo calibration is automated

//IMRPVOEMENTS: need to tune throttle sensitivity by manupulating the time-averaging array size as well as the step number increase/decrease

#include <MCP4261.h>
#include <SPI.h>
#define array_size    3
#define ch_throttle   1
#define ch_yaw        2
#define ch_pitch      3
#define ch_roll       4 
#define arm_V         3
#define maxV_stick    2.6
#define minV_stick    0
#define midV_stick    1.6   // supplies 1.65 V to pitch and roll channels
#define maxvolts      5.06
#define FloatV        1.4
#define portnum_throttle  10
#define portnum_yaw       9
#define portnum_pitch     8
#define portnum_roll      7

//***PIN ASSIGNMENTS***//

#define SWITCH_CONFIG_PIN 11  //Config jumper
// Then choose any other free pin as the Slave Select (pin 10 if the default but doesnt have to be)
#define MCP4261_SLAVE_SELECT_PIN 10 //arduino   <->   Chip Select               -> CS  (Pin 01 on MCP4261 DIP)

#define CS1_PIN 10
#define CS2_PIN 9
#define CS3_PIN 8
#define CS4_PIN 7
#define LED_PIN 5

float   volt_throttle = minV_stick; //set up neutral volt for throttle (up or down)
float   volt_yaw      = midV_stick; //set up neutral volt for yaw (CW and CCW)
float   volt_pitch    = midV_stick; //forward and backward
float   volt_roll     = midV_stick; //left and right
int     Arm           = 3;          //flag for arming the drone, should be 3 for arming, swith to 1 to gyro calibration
int     array_val[array_size];
int     i;
int     j;
float   sp_avg;
float   sp_sum;
bool    Flag_calib = 0;

// Generally, you should use "unsigned long" for variables that hold time
// The value will quickly become too large for an int to store
unsigned long previousMillis = 0;        // will store last time LED_PIN was updated

// constants won't change:
const long interval = 500;           // interval at which to blink (milliseconds)

#define DEBUG_BT true
// #define DEBUG_XY_INPUT
// #define DEBUG_SP_INPUT
#define DEBUG_DP                  // DP = digital potentiometer

#define PACKET_CONTENT_SIZE 9  //Content size for raw bluetooth packets

// Its recommended to measure the rated end-end resistance (terminal A to terminal B)
// Because this can vary by a large margin, up to -+ 20%. And temperature variations.
float rAB_ohms = 5090.00; // 5k Ohm

// Instantiate Mcp4261 object, with default rW (=117.5 ohm, its typical resistance)
MCP4261 Mcp4261 = MCP4261( MCP4261_SLAVE_SELECT_PIN, rAB_ohms );

//float initThrottleOhms = 2340.0;
//float initSteeringOhms = 2200.0;


// stepped throttle control
#define THROTTLE_STEPS 8

//===== Set up MCP4161 variables =======//
byte address = 0x00;

bool flag__first = 0;
int port;
float voltsin;
long stepnum;
int  timer_1s;
bool Flag_check;
bool Flag_Floating;
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

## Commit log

2020-01-29 Modified the software to work with Arduino Micro
2020-01-29 Added the enclosure STL files
    [Enclosure_Enclosure_Don v5_Bottom_Enclosure.stl, Enclosure_Enclosure_Don v5_Top_Enclosure.stl]
2020-01-30 Added Schematics and connection on Fritzing and Eagle
    [Liploft_Breadboard.fzz, Liploft_Schematics.sch]
2020-01-30 Changed housing file names
    [Liploft_Bottom_Housing.stl, Liploft_Top_Housing.stl]
2020-01-30 Added the lipsync housing files
    [LipSync_Button.stl, LipSync_Joystick_Base.STL, LipSync_Joystick_Front.STL, LipSync_Joystick_Rocker.STL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]
2020-01-30 Changed STL files
    [Liploft_Bottom.stl, Liploft_Top.stl]
2020-01-30 Added lipsync files
    [LipSync_Front_Housing.STL]
2020-01-30 Added BOM files
    [LipLoft_BOM.csv, LipLoft_BOM.xlsx]
2020-01-30 Updated the schematics
    [Liploft_Schematics.sch]
